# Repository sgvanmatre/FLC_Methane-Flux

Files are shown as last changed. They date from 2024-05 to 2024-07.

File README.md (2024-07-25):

# Open-source Methane Flux Instrument

Methane, a potent greenhouse gas, has significantly increased in the Earth’s atmosphere since the Industrial Revolution. A considerable portion of methane emissions stems from ground-to-atmosphere methane flux, originating from sources such as landfills, geologic seeps, and agricultural activities. These emissions exhibit spatial complexity and temporal variability, posing challenges in accurate characterization and mitigation.

Quantifying methane flux from these diverse sources is hindered by the lack of affordable measurement tools suitable for widespread deployment. There is a critical need for an instrument capable of measuring flux rates spanning 0.1 to 1000 g CH4 m-2 d-1 at landfills. The ideal instrument must operate autonomously with a remote power supply, and be compact and lightweight enough for easy transport by two individuals. It should provide flux measurements at hourly intervals and support cellular data transmission.

Through a collaborative effort between Fort Lewis College and CU Boulder's air quality laboratories, a low-cost, dynamic flux chamber was developed, calibrated, and validated for measuring methane flux within the range of 0-150 g/m²-day. Methane concentrations in the sensor chamber are monitored using four low-cost metal oxide sensors: a BME 680, along with Figaro TGS sensors (2600, 2602, and 2611).

This repository includes the PCB design and the microcontroller code for the system. 

## Table of Contents

- [Usage](#usage)
- [Contributing](#contributing)
- [Credits](#credits)
- [License](#license)
- [Updating Firmware](#updating-firmware)

## Usage

We encourage everyone to use or adapt this code for their own projects. Below are some examples and instructions to help you get started.

### Tools Used

- **Eagle PCB Software:** We used Eagle PCB software for designing and testing our printed circuit boards.
- **Arduino:** Our code is compatible with the Arduino platform and was developed using the Arduino IDE and initialized on an Arduino MKR NB 1500 board. We did have to manually update the firmware. Instruction are at the bottom of this file.

### Getting Started

1. **Clone the Repository:**
   - Clone the repository to your local machine using the following command:
     ```sh
     git clone https://github.com/your-username/your-repo-name.git
     ```

2. **Open in Eagle PCB Software:**
   - Open the Eagle PCB files from the repository in Eagle PCB software to view and modify the PCB designs.

3. **Load the Code in Arduino IDE:**
   - Open the Arduino IDE.
   - Load the Arduino code from the repository into the Arduino IDE.

4. **Upload to Your Arduino Board:**
   - Connect your Arduino board to your computer.
   - Select the correct board and port from the Arduino IDE.
   - Click the "Upload" button to upload the code to your Arduino board.

## Contributing

We welcome contributions from anyone who is interested! Whether it's fixing a bug, adding a new feature, improving documentation, or any other enhancements, your help is greatly appreciated.

### How to Contribute

1. **Fork the Repository:**
   - Click the "Fork" button at the top right of this repository page to create a copy of this repository in your GitHub account.

2. **Clone Your Fork:**
   - Clone your forked repository to your local machine using the following command:
     ```sh
     git clone https://github.com/your-username/your-repo-name.git
     ```

3. **Create a New Branch:**
   - Create a new branch to work on your changes:
     ```sh
     git checkout -b your-branch-name
     ```

4. **Make Your Changes:**
   - Implement your changes in the new branch.

5. **Commit Your Changes:**
   - Commit your changes with a clear and concise commit message:
     ```sh
     git add .
     git commit -m "Description of your changes"
     ```

6. **Push Your Changes:**
   - Push your changes to your forked repository:
     ```sh
     git push origin your-branch-name
     ```

7. **Submit a Pull Request:**
   - Go to the original repository on GitHub and click the "New Pull Request" button.
   - Select your branch from your forked repository and compare it with the base repository.
   - Submit the pull request for review.

### Guidelines

- Ensure your code follows the project's style guidelines.
- Write clear, concise commit messages.
- Update documentation as necessary.
- Test your changes thoroughly before submitting a pull request.

Thank you for your interest in contributing! Together, we can make this project even better.

## Credits

Contributors

- **Principal Contributor:** [Seth VanMatre](https://github.com/sgvanmatre)
- **Summer Contributions:** [Sonie Taylor Schermer](https://github.com/tschermer02)
- **Additional Assistance:** [Max Krauss](https://github.com/maxtkrauss)

## License

This project is licensed under the MIT License - see the LICENSE file for details.

## Firmware Update Instructions

The latest SARA-R410M-02B firmware (version -04) is now available publicly on the product page:

[Product Page - SARA-R4 Series](https://www.u-blox.com/en/product/sara-r4-series?legacy=Current#Documentation-&-resources)

A direct download to the firmware files is available here:

[Direct Download - Firmware Files](https://content.u-blox.com/sites/default/files/2023-06/SARA-R410M-02B-04-P1-L0000000512A0221-000K00.zip?_ga=2.26117621.998416448.1694721819-824184379.1689262389)

The recommended method is to update via the native USB port of the SARA-R4 module using our Windows tool "EasyFlash".

To download the correct EasyFlash tool, refer to the link in the PCN to the most up-to-date/recommended version in the section "Tools."

A link to the latest (version -04) PCN is available here:

[PCN - Version -04](https://content.u-blox.com/sites/default/files/documents/SARA-R410M-02B-04_PCN_UBX-22005059.pdf)

For updating the firmware, an application note is available here:

[Application Note - Firmware Update](https://www.u-blox.com/sites/default/files/SARA-R4-FW-Update_AppNote_UBX-17049154.pdf)

### Additional Resources for 3rd Party Boards

- **Arduino MKR NB 1500 USB test points:**
  [Forum Discussion](https://forum.arduino.cc/t/firmware-upgrade-for-ublox-sara-r410m-02b-on-the-mkr-nb-1500-2/699292)

- **Particle Boron:**
  [Community Guide](https://community.particle.io/t/how-to-load-ublox-firmware-upgrade-for-sara-r410-lte-on-the-boron/51769)

- **Sparkfun LTE M1 Shield enable USB:**
  [Hookup Guide](https://learn.sparkfun.com/tutorials/lte-cat-m1nb-iot-shield-hookup-guide?_gl=1*pm7rgo*_ga*NDUwNDc5ODYxLjE2OTMyNDMzMjk.*_ga_T369JS7J9N*MTY5NDc5ODg0My4yLjAuMTY5NDc5ODg0My42MC4wLjA.&_ga=2.145880316.975271267.1694798844-450479861.1693243329#USB-interface)

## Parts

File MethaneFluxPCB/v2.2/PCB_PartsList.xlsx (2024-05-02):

Qty | Value | Package | Parts | URL
2 | 1.0uF (https://www.digikey.com/product-detail/en/samsung-electro-mechanics/CL10A105KP8NNNC/1276-1182-1-ND/3889268) | 603 | C7, C14 | https://www.digikey.com/product-detail/en/samsung-electro-mechanics/CL10A105KP8NNNC/1276-1182-1-ND/3889268
14 | 10k (https://www.digikey.com/en/products/detail/stackpole-electronics-inc/RMCF0603JT10K0/1758104) | 603 | R14, R15, R16, R17, R20, R21, R22, R23, R24, R25, R26, R27, R28, R29 | https://www.digikey.com/en/products/detail/stackpole-electronics-inc/RMCF0603JT10K0/1758104
8 | 10uF (https://www.digikey.com/en/products/detail/samsung-electro-mechanics/CL10A106MQ8NNNC/3886777) | 603 | C5, C6, C8, C9, C20, C22, C23, C24 | https://www.digikey.com/en/products/detail/samsung-electro-mechanics/CL10A106MQ8NNNC/3886777
2 | 282836-5 (https://www.digikey.com/en/products/detail/te-connectivity-amp-connectors/282836-5/1826942) | TE_282836-5 | J1, J2 | https://www.digikey.com/en/products/detail/te-connectivity-amp-connectors/282836-5/1826942
1 | 282837-2 (https://www.digikey.com/en/products/detail/te-connectivity-amp-connectors/282836-2/1826939) | TE_282837-2 | P1 | https://www.digikey.com/en/products/detail/te-connectivity-amp-connectors/282836-2/1826939
2 | 2N7002DW (https://www.digikey.com/en/products/detail/onsemi/2N7002DW/1785764) | SOT363 | U$3, U$4 | https://www.digikey.com/en/products/detail/onsemi/2N7002DW/1785764
4 | 3.3k (https://www.digikey.com/en/products/detail/koa-speer-electronics-inc/RK73H1JRTTD3301F/12314776) | 603 | R6, R7, R8, R9 | https://www.digikey.com/en/products/detail/koa-speer-electronics-inc/RK73H1JRTTD3301F/12314776
4 | 30Ω/1.8A (https://www.digikey.com/en/products/detail/murata-electronics/BLM18EG221SN1D/1016151) | 603 | FB1, FB2, FB3, FB4 | https://www.digikey.com/en/products/detail/murata-electronics/BLM18EG221SN1D/1016151
4 | 4.7k (https://www.digikey.com/en/products/detail/yageo/RC0402JR-074K7L/726477) | 603 | R10, R11, R13, R30 | https://www.digikey.com/en/products/detail/yageo/RC0402JR-074K7L/726477
8 | 470 (https://www.digikey.com/product-detail/en/RC0603JR-07470RL/311-470GRTR-ND/726791/?itemSeq=327776216) | 603 | R1, R2, R3, R4, R5, R12, R18, R19 | https://www.digikey.com/product-detail/en/RC0603JR-07470RL/311-470GRTR-ND/726791/?itemSeq=327776216
1 | 74LVC125APW,118 (https://www.digikey.com/en/products/detail/nexperia-usa-inc/74LVC125APW-118/946678) | IC_74LVC125APW,118 | U3 | https://www.digikey.com/en/products/detail/nexperia-usa-inc/74LVC125APW-118/946678
2 | ADS1115IDGSR (https://www.digikey.com/en/products/detail/texas-instruments/ADS1115IDGSR/2231567) | SOP50P490X110-10N | U1, U5 | https://www.digikey.com/en/products/detail/texas-instruments/ADS1115IDGSR/2231567
1 | BAT-HLD-001 (https://www.digikey.com/en/products/detail/te-connectivity-linx/BAT-HLD-001/1577235) | BAT_BAT-HLD-001 | BT1 | https://www.digikey.com/en/products/detail/te-connectivity-linx/BAT-HLD-001/1577235
2 | BME680 (https://www.digikey.com/en/products/detail/bosch-sensortec/BME680/7401317) | PSON80P300X300X100-8N | U2, U4 | https://www.digikey.com/en/products/detail/bosch-sensortec/BME680/7401317
1 | DS3231/SO (https://www.digikey.com/en/products/detail/analog-devices-inc-maxim-integrated/DS3231S-T-R/1197575) | SO16W | IC1 | https://www.digikey.com/en/products/detail/analog-devices-inc-maxim-integrated/DS3231S-T-R/1197575
1 | GTFH08131YHR (https://www.digikey.com/en/products/detail/amphenol-cs-commercial-products/GTFH08131YHR/7057320) | AMPHENOL_GTFH08131YHR | J3 | https://www.digikey.com/en/products/detail/amphenol-cs-commercial-products/GTFH08131YHR/7057320
1 | IN_47UH_3.8A_SMD (https://www.digikey.com/en/products/detail/w-rth-elektronik/7447709470/1639307) | INDUCTOR_4X4MM | US1 | https://www.digikey.com/en/products/detail/w-rth-elektronik/7447709470/1639307
1 | IN_33UH_3.8A_SMD (https://www.digikey.com/en/products/detail/w-rth-elektronik/7447709470/1639307) | INDUCTOR_4X4MM | U$7 | https://www.digikey.com/en/products/detail/w%C3%BCrth-elektronik/7447709330/1638649
1 | LM2596S-5 (https://www.digikey.com/en/products/detail/texas-instruments/LM2596S-5-0-NOPB/334842) | VREG_LM2596S-5 | U6 | https://www.digikey.com/en/products/detail/texas-instruments/LM2596S-5-0-NOPB/334842
2 | LM2596S-3.3 (https://www.digikey.com/en/products/detail/texas-instruments/LM2596S-3-3/3701219) | VREG_LM2596S-3.3 | U7 | https://www.digikey.com/en/products/detail/texas-instruments/LM2596S-3-3/3701219
1 | MKRNB1500 (https://www.digikey.com/en/products/detail/arduino/ABX00019/9486709) | MRKNB1500 | U$5 | https://www.digikey.com/en/products/detail/arduino/ABX00019/9486709
1 | RB141C1100 (https://www.digikey.com/en/products/detail/e-switch/RB141C1100/3778081) | SW_RB141C1100 | S1 | https://www.digikey.com/en/products/detail/e-switch/RB141C1100/3778081
2 | Yellow (https://www.digikey.com/en/products/detail/w%C3%BCrth-elektronik/150060YS75000/4489907) | LED-0603 | D1, D3 | https://www.digikey.com/en/products/detail/w%C3%BCrth-elektronik/150060YS75000/4489907
2 | SS34_214AB (https://www.digikey.com/product-detail/en/on-semiconductor/SS34/SS34FSCT-ND/2094459) | SOD-323 | U$2, U$6 | https://www.digikey.com/product-detail/en/on-semiconductor/SS34/SS34FSCT-ND/2094459
2 | TAJC227K006RNJ (https://www.digikey.com/en/products/detail/kyocera-avx/TAJC227K006RNJ/563818) | CAPPM6032X280N | C1, C2 | https://www.digikey.com/en/products/detail/kyocera-avx/TAJC227K006RNJ/563818
2 | TAJD107K016RNJ (https://www.digikey.com/en/products/detail/kyocera-avx/TAJD107K016RNJ/563828) | CAPPM7344X310N | C3, C4 | https://www.digikey.com/en/products/detail/kyocera-avx/TAJD107K016RNJ/563828
2 | TGS2600 | TO255P920H830-4 | A1-00, A2-00
2 | TGS2602 | TGS2602 | A3-02, A4-02
2 | TGS2611 | TGS2611 | A5-11, A6-11
4 | VJ0603Y104KLXAC5G (https://www.digikey.com/en/products/detail/nextgen-components/0603B103K500SD/14632393) | CAPC1608X92N | C16, C17, C18, C19 | https://www.digikey.com/en/products/detail/nextgen-components/0603B103K500SD/14632393

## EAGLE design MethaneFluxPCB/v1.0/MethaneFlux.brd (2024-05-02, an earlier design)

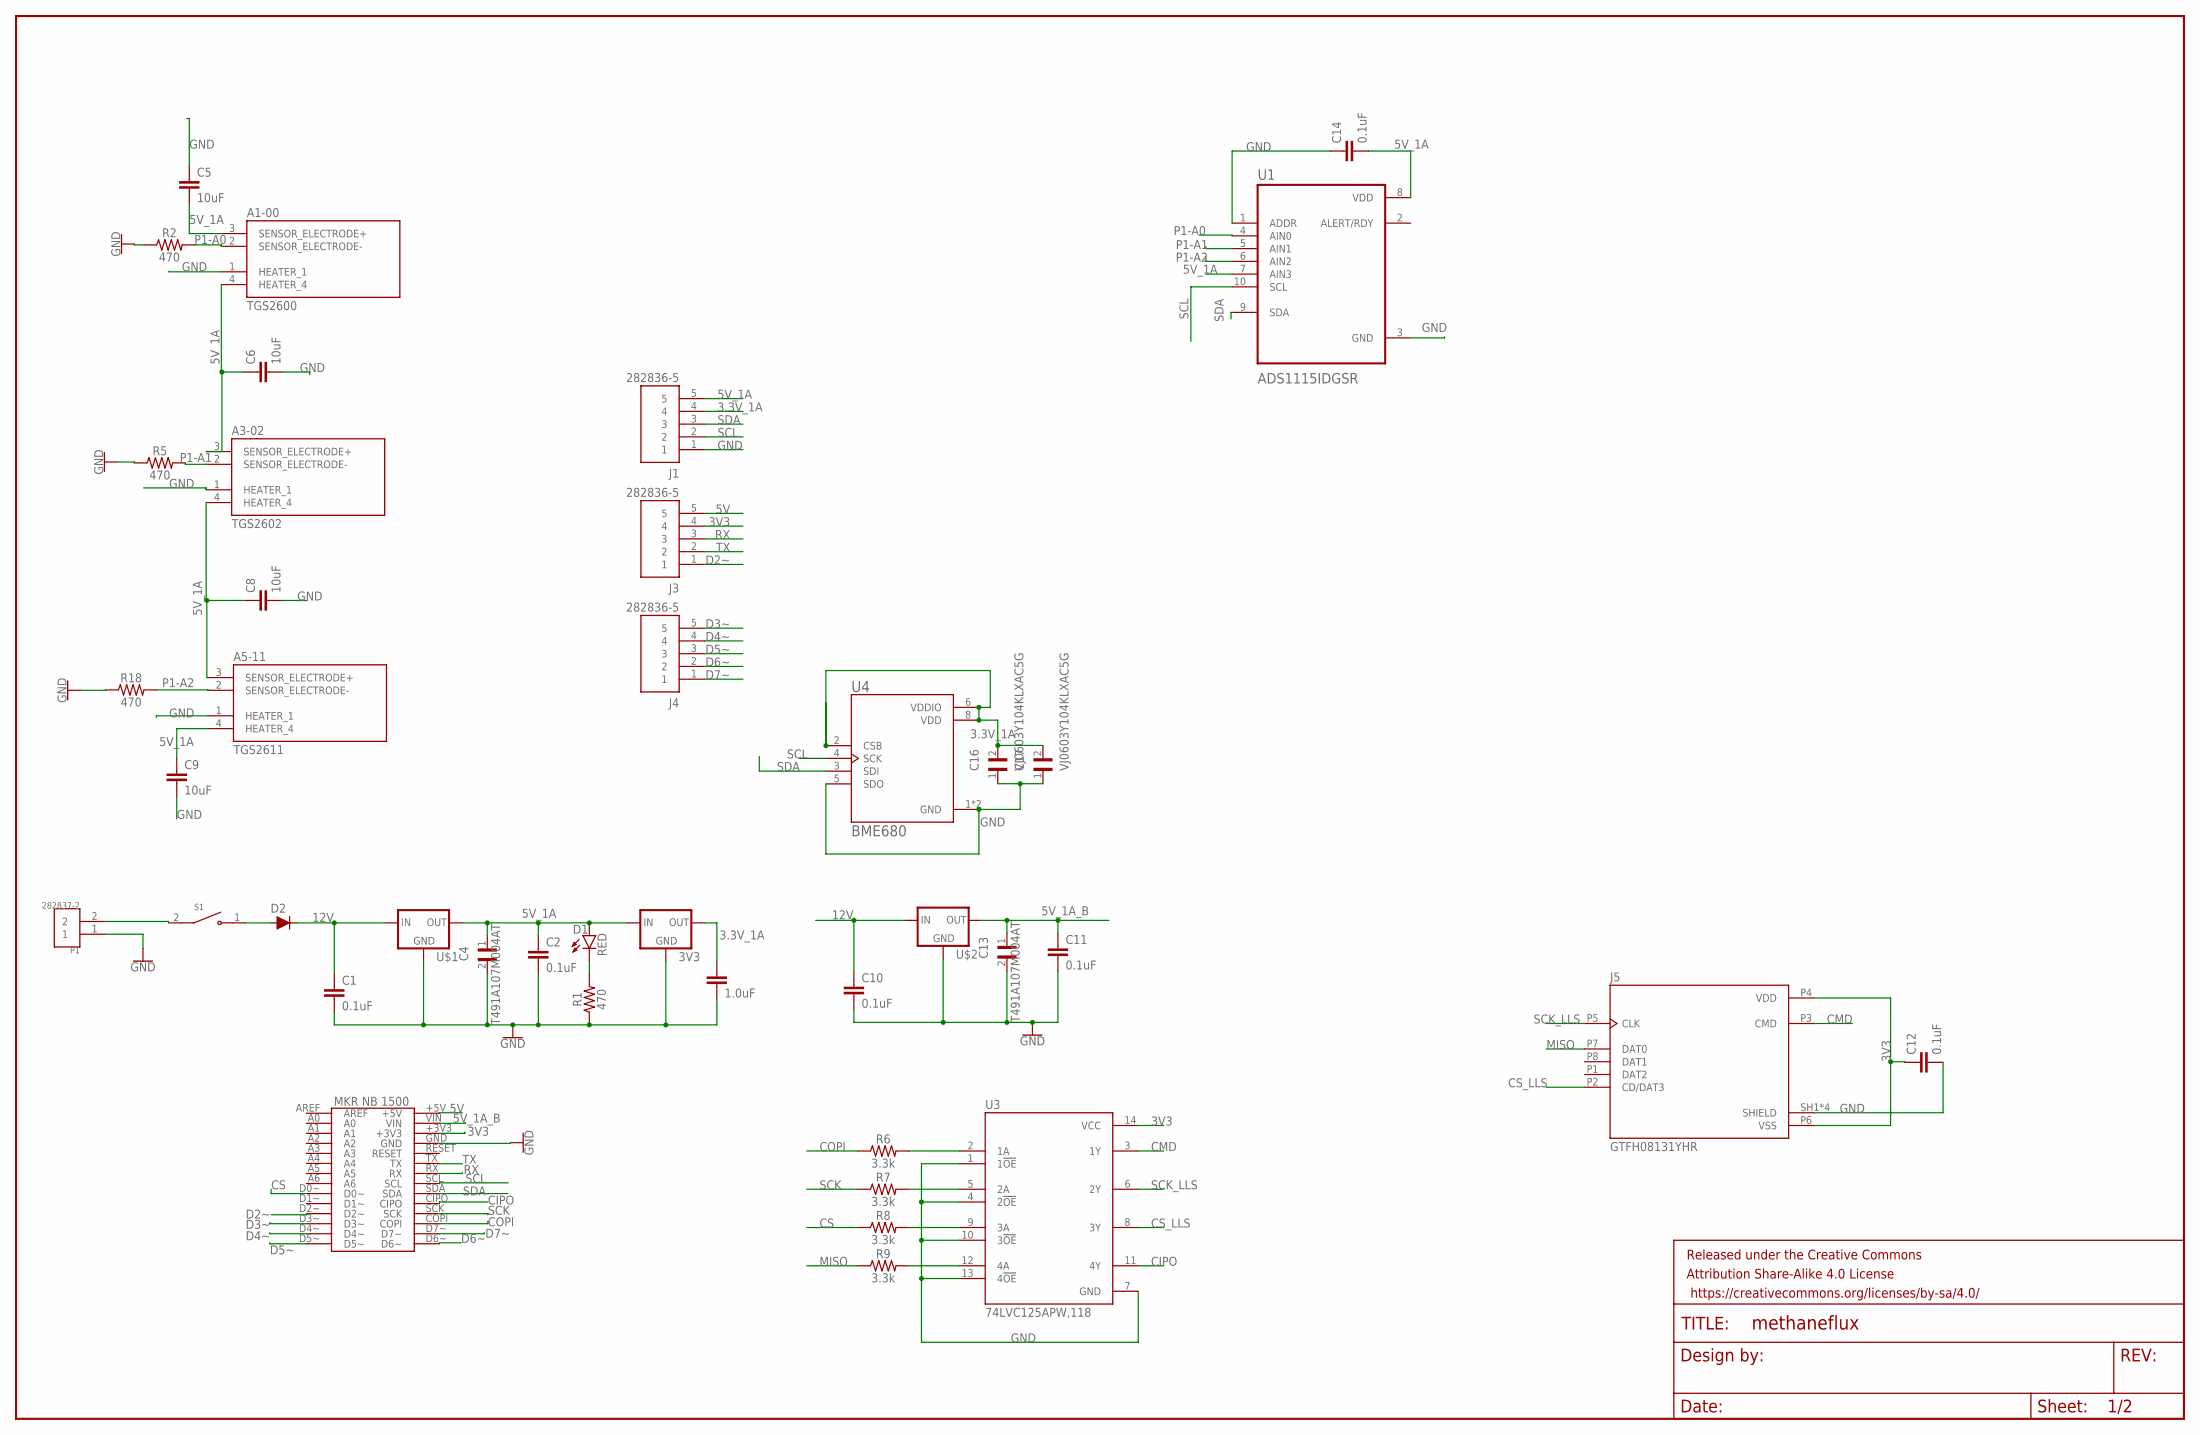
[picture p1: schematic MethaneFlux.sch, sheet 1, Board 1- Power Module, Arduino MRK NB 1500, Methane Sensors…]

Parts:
3V3: V_REG_LD1117VXXLD1117-SMD; SOT223
A1-00: TGS2600; TO255P920H830-4
A3-02: TGS2602
A5-11: TGS2611
C1, C2, C10, C11, C12, C14: 0.1uF; 0603
C3: 1.0uF; 0603
C4, C13: T491A107M004AT; CAPC3216X110N
C5, C6, C8, C9: 10uF; 0603
C16, C17: VJ0603Y104KLXAC5G; CAPC1608X92N
D1: RED; LED-0603
D2: 200mA/100V/1V; DIODE-1N4148
FRAME1: FRAME-LEDGER; CREATIVE_COMMONS
J1, J3, J4: 282836-5; TE_282836-5
J5: GTFH08131YHR; AMPHENOL_GTFH08131YHR
P1: 282837-2; TE_282837-2
R1, R2, R5, R18: 470; 0603
R6, R7, R8, R9: 3.3k; 0603
S1: RB141C1100; SW_RB141C1100
U1: ADS1115IDGSR; SOP50P490X110-10N
U3: 74LVC125APW,118; IC_74LVC125APW,118
U4: BME680; PSON80P300X300X100-8N
U$1, U$2: V_REG_LD1117VXXLD1117-SMD; SOT223
U$5: MKRNB1500; MRKNB1500

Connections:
3.3V_1A: 3V3.2 (OUT), C3.1, C16.2, C17.2, J1.4, U4.2 (CSB), U4.6 (VDDIO), U4.8 (VDD)
3V3: C12.1, J3.4, J5.P4 (VDD), J5.P6 (VSS), U3.14 (VCC), U$5.+3V3
5V: J3.5, U$5.+5V
5V_1A: 3V3.3 (IN), A1-00.3 (SENSOR_ELECTRODE+), A1-00.4 (HEATER_4), A3-02.3 (SENSOR_ELECTRODE+), A3-02.4 (HEATER_4), A5-11.3 (SENSOR_ELECTRODE+), A5-11.4 (HEATER_4), C2.1, C4.1, C5.2, C6.1, C8.1, C9.1, C14.2, D1.A, J1.5, U1.7 (AIN3), U1.8 (VDD), U$1.2 (OUT)
5V_1A_B: C11.1, C13.1, U$2.2 (OUT), U$5.VIN
12V: C1.1, C10.1, D2.C, U$1.3 (IN), U$2.3 (IN)
CIPO: U3.11 (4Y), U$5.CIPO
CMD: J5.P3 (CMD), U3.3 (1Y)
COPI: R6.1, U$5.COPI
CS: R8.1, U$5.D0~
CS_LLS: J5.P2 (CD/DAT3), U3.8 (3Y)
D2~: J3.1, U$5.D2~
D3~: J4.5, U$5.D3~
D4~: J4.4, U$5.D4~
D5~: J4.3, U$5.D5~
D6~: J4.2, U$5.D6~
D7~: J4.1, U$5.D7~
GND: 3V3.1 (GND), A1-00.1 (HEATER_1), A3-02.1 (HEATER_1), A5-11.1 (HEATER_1), C1.2, C2.2, C3.2, C4.2, C5.1, C6.2, C8.2, C9.2, C10.2, C11.2, C12.2, C13.2, C14.1, C16.1, C17.1, J1.1, J5.SH1 (SHIELD), J5.SH2 (SHIELD), J5.SH3 (SHIELD), J5.SH4 (SHIELD), P1.1, R1.1, R2.1, R5.1, R18.1, U1.1 (ADDR), U1.3 (GND), U3.1 (1!OE), U3.4 (2!OE), U3.7 (GND), U3.10 (3!OE), U3.13 (4!OE), U4.1 (GND), U4.5 (SDO), U4.7 (GND), U$1.1 (GND), U$2.1 (GND), U$5.GND
MISO: J5.P7 (DAT0), R9.1
unnamed: R6.2, U3.2 (1A)
unnamed: D1.C, R1.2
unnamed: R7.2, U3.5 (2A)
unnamed: P1.2, S1.2
unnamed: D2.A, S1.1
unnamed: R8.2, U3.9 (3A)
unnamed: R9.2, U3.12 (4A)
P1-A0: A1-00.2 (SENSOR_ELECTRODE-), R2.2, U1.4 (AIN0)
P1-A1: A3-02.2 (SENSOR_ELECTRODE-), R5.2, U1.5 (AIN1)
P1-A2: A5-11.2 (SENSOR_ELECTRODE-), R18.2, U1.6 (AIN2)
RX: J3.3, U$5.RX
SCK: R7.1, U$5.SCK
SCK_LLS: J5.P5 (CLK), U3.6 (2Y)
SCL: J1.2, U1.10 (SCL), U4.4 (SCK), U$5.SCL
SDA: J1.3, U1.9 (SDA), U4.3 (SDI), U$5.SDA
TX: J3.2, U$5.TX

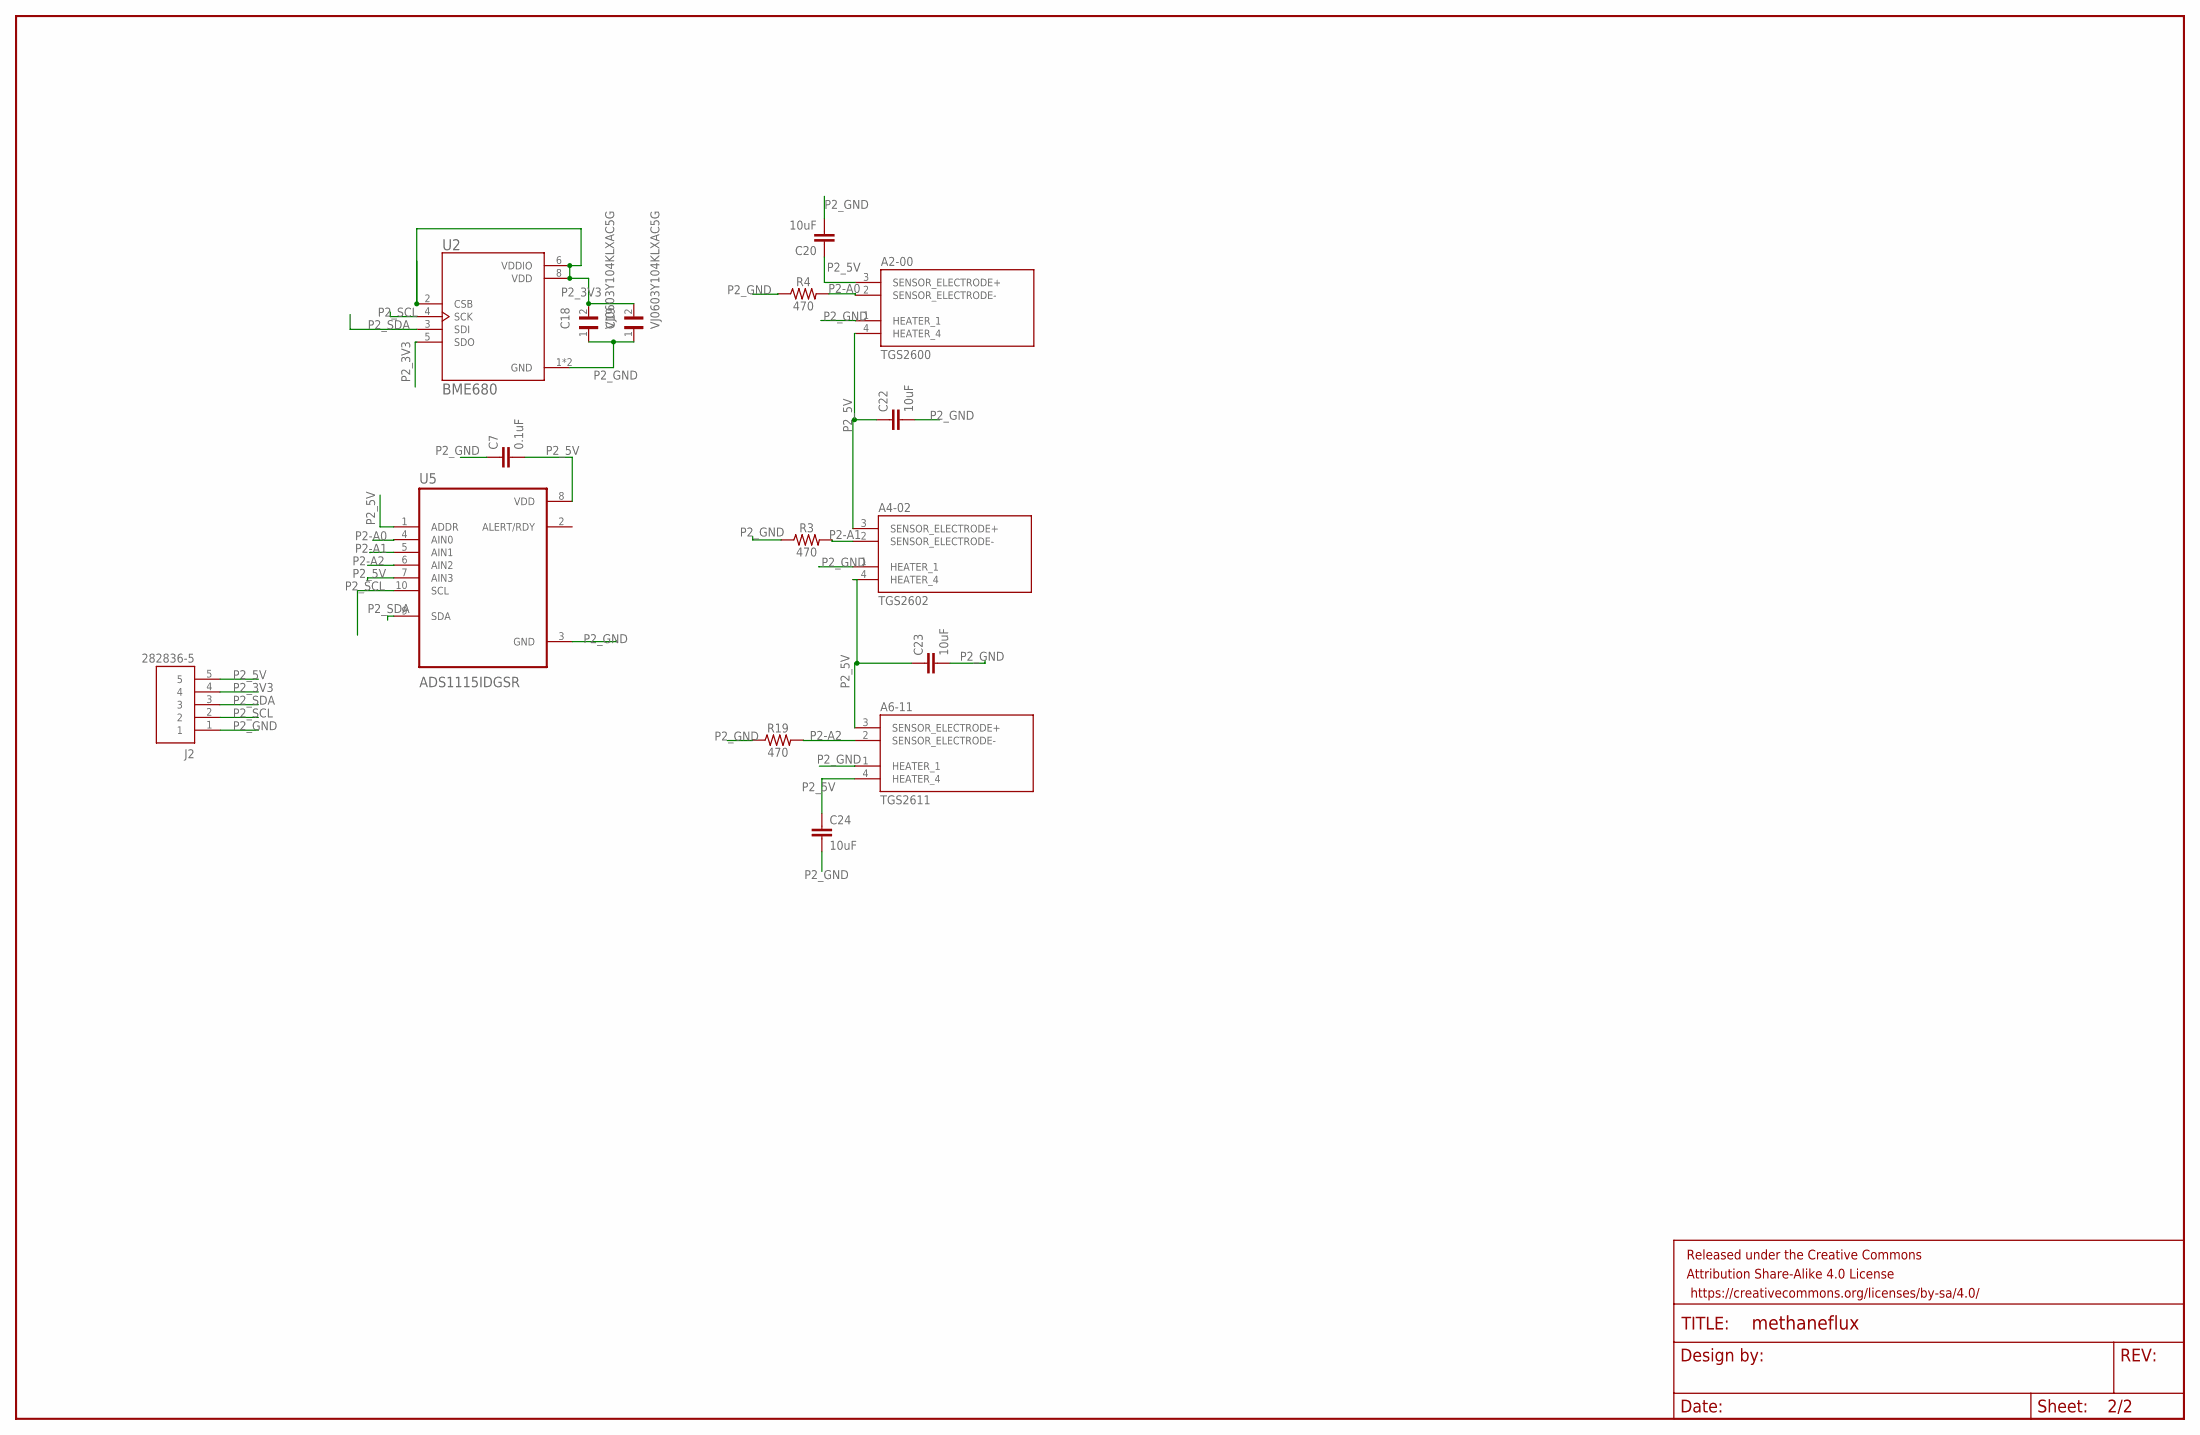
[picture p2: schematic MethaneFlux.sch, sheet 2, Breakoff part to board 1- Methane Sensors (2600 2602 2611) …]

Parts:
A2-00: TGS2600; TO255P920H830-4
A4-02: TGS2602
A6-11: TGS2611
C7: 0.1uF; 0603
C18, C19: VJ0603Y104KLXAC5G; CAPC1608X92N
C20, C22, C23, C24: 10uF; 0603
FRAME2: FRAME-LEDGER; CREATIVE_COMMONS
J2: 282836-5; TE_282836-5
R3, R4, R19: 470; 0603
U2: BME680; PSON80P300X300X100-8N
U5: ADS1115IDGSR; SOP50P490X110-10N

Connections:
P2-A0: A2-00.2 (SENSOR_ELECTRODE-), R4.2, U5.4 (AIN0)
P2-A1: A4-02.2 (SENSOR_ELECTRODE-), R3.2, U5.5 (AIN1)
P2-A2: A6-11.2 (SENSOR_ELECTRODE-), R19.2, U5.6 (AIN2)
P2_3V3: C18.2, C19.2, J2.4, U2.2 (CSB), U2.5 (SDO), U2.6 (VDDIO), U2.8 (VDD)
P2_5V: A2-00.3 (SENSOR_ELECTRODE+), A2-00.4 (HEATER_4), A4-02.3 (SENSOR_ELECTRODE+), A4-02.4 (HEATER_4), A6-11.3 (SENSOR_ELECTRODE+), A6-11.4 (HEATER_4), C7.2, C20.1, C22.1, C23.1, C24.1, J2.5, U5.1 (ADDR), U5.7 (AIN3), U5.8 (VDD)
P2_GND: A2-00.1 (HEATER_1), A4-02.1 (HEATER_1), A6-11.1 (HEATER_1), C7.1, C18.1, C19.1, C20.2, C22.2, C23.2, C24.2, J2.1, R3.1, R4.1, R19.1, U2.1 (GND), U2.7 (GND), U5.3 (GND)
P2_SCL: J2.2, U2.4 (SCK), U5.10 (SCL)
P2_SDA: J2.3, U2.3 (SDI), U5.9 (SDA)

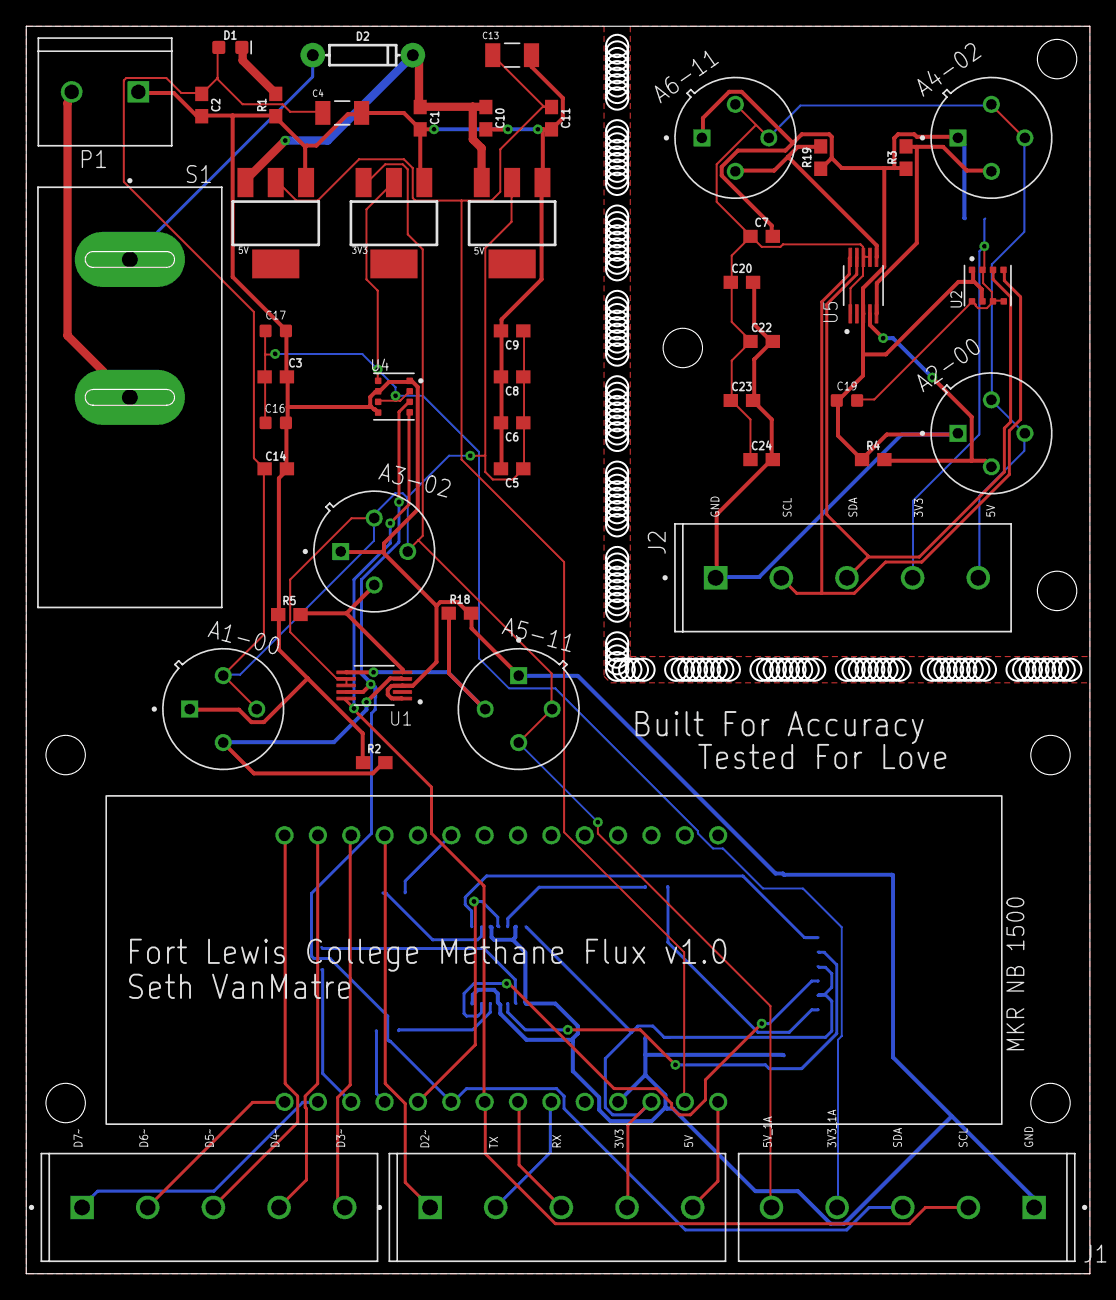
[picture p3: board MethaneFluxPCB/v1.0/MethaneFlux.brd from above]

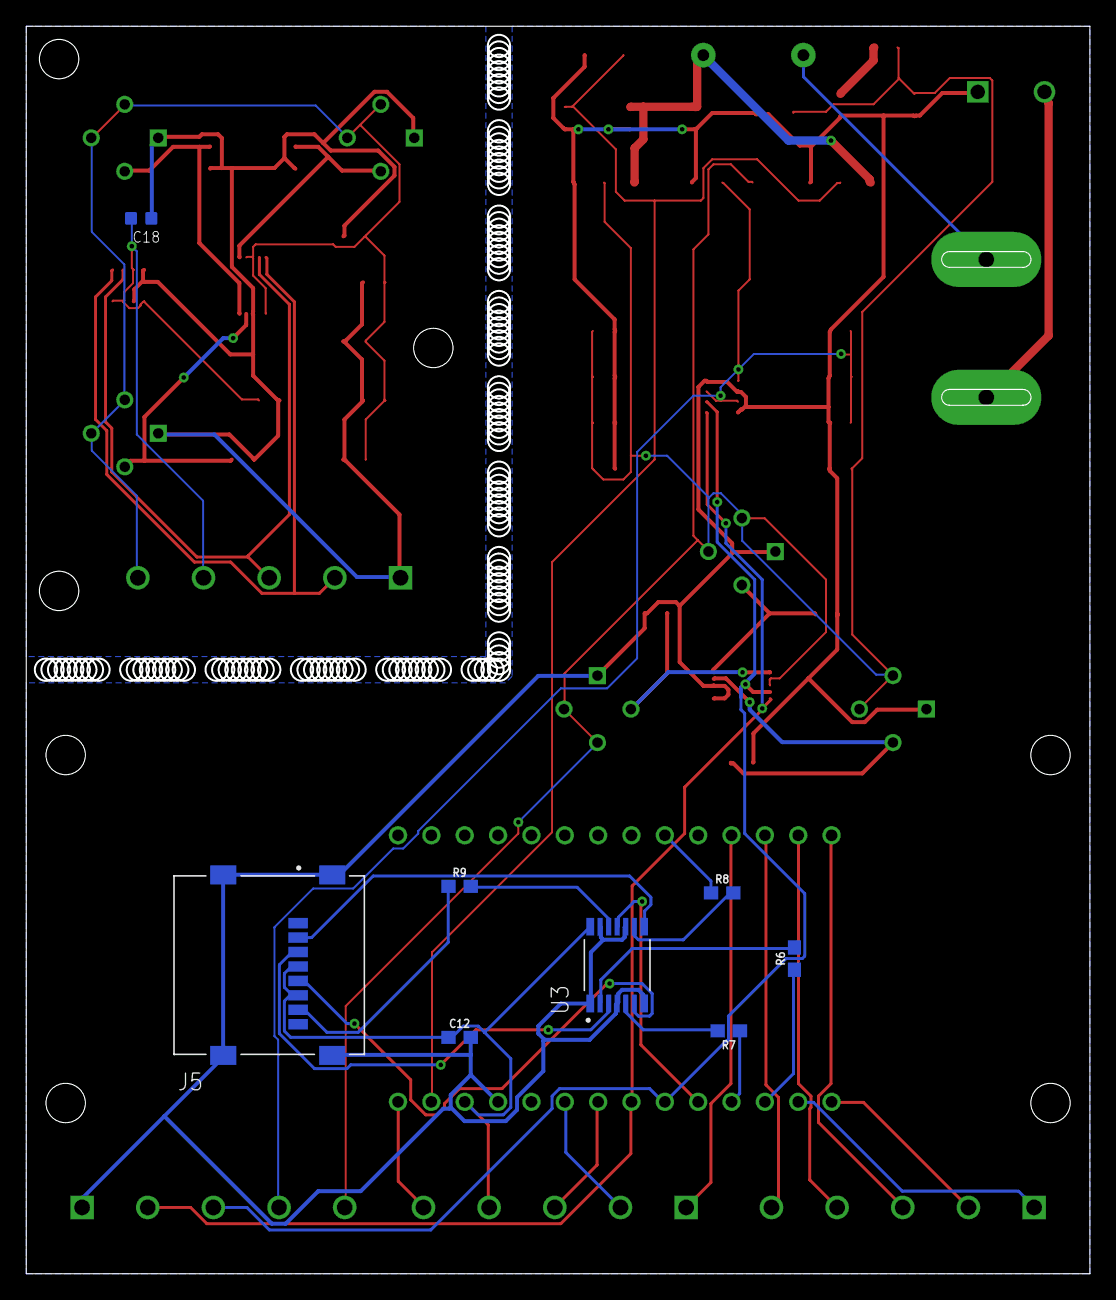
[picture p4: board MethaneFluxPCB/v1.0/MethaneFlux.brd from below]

Board: 2 copper layers, 81.0 x 95.0 mm, 59 parts (8 on the bottom side), 43 nets.

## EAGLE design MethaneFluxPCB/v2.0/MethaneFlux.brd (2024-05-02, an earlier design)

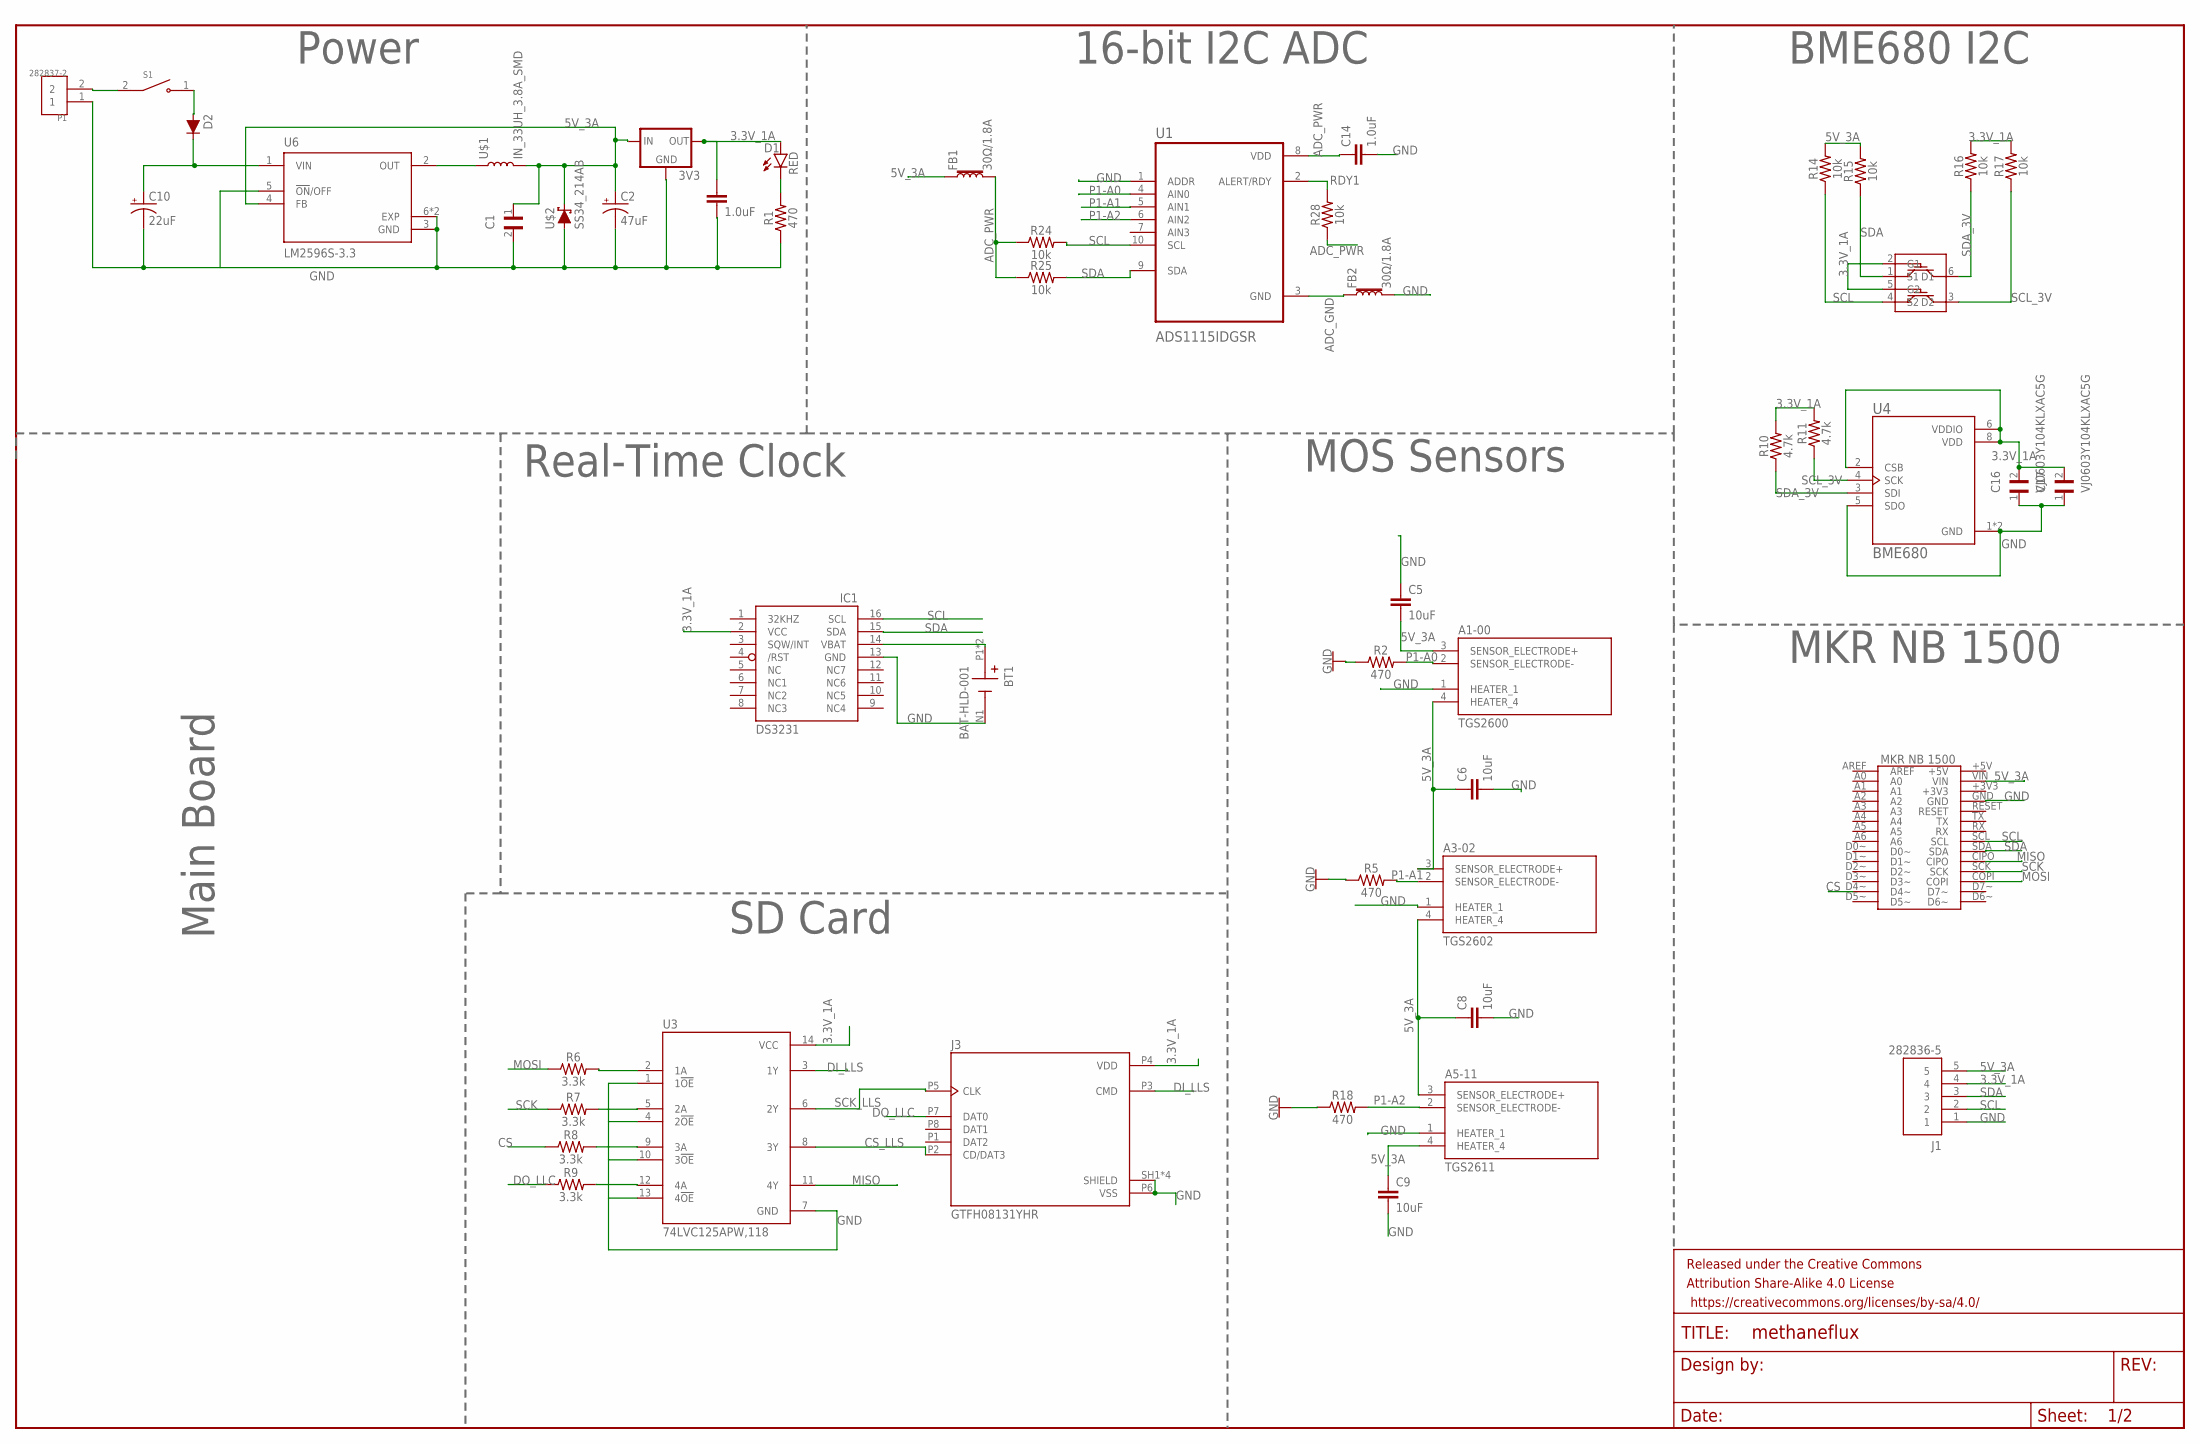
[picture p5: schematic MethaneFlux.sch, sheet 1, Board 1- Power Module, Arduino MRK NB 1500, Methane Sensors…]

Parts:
3V3: V_REG_LD1117VXXLD1117-SMD; SOT223
A1-00: TGS2600; TO255P920H830-4
A3-02: TGS2602
A5-11: TGS2611
BT1: BAT-HLD-001; BAT_BAT-HLD-001
C1: T491A107M004AT; CAPC3216X110N
C2: 47uF; PANASONIC_D
C3, C14: 1.0uF; 0603
C5, C6, C8, C9: 10uF; 0603
C10: 22uF; PANASONIC_C
C16, C17: VJ0603Y104KLXAC5G; CAPC1608X92N
D1: RED; LED-0603
D2: 200mA/100V/1V; DIODE-1N4148
FB1, FB2: 30Ω/1.8A; 0603
FRAME1: FRAME-LEDGER; CREATIVE_COMMONS
IC1: DS3231/SO; SO16W
J1: 282836-5; TE_282836-5
J3: GTFH08131YHR; AMPHENOL_GTFH08131YHR
P1: 282837-2; TE_282837-2
R1, R2, R5, R18: 470; 0603
R6, R7, R8, R9: 3.3k; 0603
R10, R11: 4.7k; 0603
R14, R15, R16, R17, R24, R25, R28: 10k; 0603
S1: RB141C1100; SW_RB141C1100
U1: ADS1115IDGSR; SOP50P490X110-10N
U3: 74LVC125APW,118; IC_74LVC125APW,118
U4: BME680; PSON80P300X300X100-8N
U6: LM2596S-3.3; VREG_LM2596S-3.3
U$1: IN_33UH_3.8A_SMD; INDUCTOR_4X4MM
U$2: SS34_214AB; SOD-323
U$3: 2N7002DW; SOT363
U$5: MKRNB1500; MRKNB1500

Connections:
3.3V_1A: 3V3.2 (OUT), C3.1, C16.2, C17.2, D1.A, IC1.2 (VCC), J1.4, J3.P4 (VDD), R10.2, R11.2, R16.2, R17.2, U3.14 (VCC), U4.2 (CSB), U4.6 (VDDIO), U4.8 (VDD), U$3.2 (G1), U$3.5 (G2)
5V_3A: 3V3.3 (IN), A1-00.3 (SENSOR_ELECTRODE+), A1-00.4 (HEATER_4), A3-02.3 (SENSOR_ELECTRODE+), A3-02.4 (HEATER_4), A5-11.3 (SENSOR_ELECTRODE+), A5-11.4 (HEATER_4), C1.1, C2.+, C5.2, C6.1, C8.1, C9.1, FB1.1, J1.5, R14.2, R15.2, U6.4 (FB), U$1.P$2 (2), U$2.C, U$5.VIN
ADC_GND: FB2.1, U1.3 (GND)
ADC_PWR: C14.1, FB1.2, R24.1, R25.1, R28.1, U1.8 (VDD)
CS: R8.1, U$5.D4~
CS_LLS: J3.P2 (CD/DAT3), U3.8 (3Y)
DI_LLS: J3.P3 (CMD), U3.3 (1Y)
DO_LLC: J3.P7 (DAT0), R9.1
GND: 3V3.1 (GND), A1-00.1 (HEATER_1), A3-02.1 (HEATER_1), A5-11.1 (HEATER_1), BT1.N1 (-), C1.2, C2.-, C3.2, C5.1, C6.2, C8.2, C9.2, C10.-, C14.2, C16.1, C17.1, FB2.2, IC1.13 (GND), J1.1, J3.P6 (VSS), J3.SH1 (SHIELD), J3.SH2 (SHIELD), J3.SH3 (SHIELD), J3.SH4 (SHIELD), P1.1, R1.1, R2.1, R5.1, R18.1, U1.1 (ADDR), U3.1 (1!OE), U3.4 (2!OE), U3.7 (GND), U3.10 (3!OE), U3.13 (4!OE), U4.1 (GND), U4.5 (SDO), U4.7 (GND), U6.3 (GND), U6.5 (!ON!/OFF), U6.6 (EXP), U6.7 (EXP), U$2.A, U$5.GND
MISO: U3.11 (4Y), U$5.CIPO
MOSI: R6.1, U$5.COPI
unnamed: R6.2, U3.2 (1A)
unnamed: P1.2, S1.2
unnamed: D2.A, S1.1
unnamed: R7.2, U3.5 (2A)
unnamed: R8.2, U3.9 (3A)
unnamed: R9.2, U3.12 (4A)
unnamed: U6.2 (OUT), U$1.P$1 (1)
unnamed: BT1.P1 (+), BT1.P2 (+), IC1.14 (VBAT)
unnamed: C10.+, D2.C, U6.1 (VIN)
unnamed: D1.C, R1.2
P1-A0: A1-00.2 (SENSOR_ELECTRODE-), R2.2, U1.4 (AIN0)
P1-A1: A3-02.2 (SENSOR_ELECTRODE-), R5.2, U1.5 (AIN1)
P1-A2: A5-11.2 (SENSOR_ELECTRODE-), R18.2, U1.6 (AIN2)
RDY1: R28.2, U1.2 (ALERT/RDY)
SCK: R7.1, U$5.SCK
SCK_LLS: J3.P5 (CLK), U3.6 (2Y)
SCL: IC1.16 (SCL), J1.2, R14.1, R24.2, U1.10 (SCL), U$3.4 (S2), U$5.SCL
SCL_3V: R11.1, R17.1, U4.4 (SCK), U$3.3 (D2)
SDA: IC1.15 (SDA), J1.3, R15.1, R25.2, U1.9 (SDA), U$3.1 (S1), U$5.SDA
SDA_3V: R10.1, R16.1, U4.3 (SDI), U$3.6 (D1)

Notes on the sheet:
MKR NB 1500
MOS Sensors
BME680 I2C
16-bit I2C ADC
Power
Real-Time Clock
SD Card
Main Board

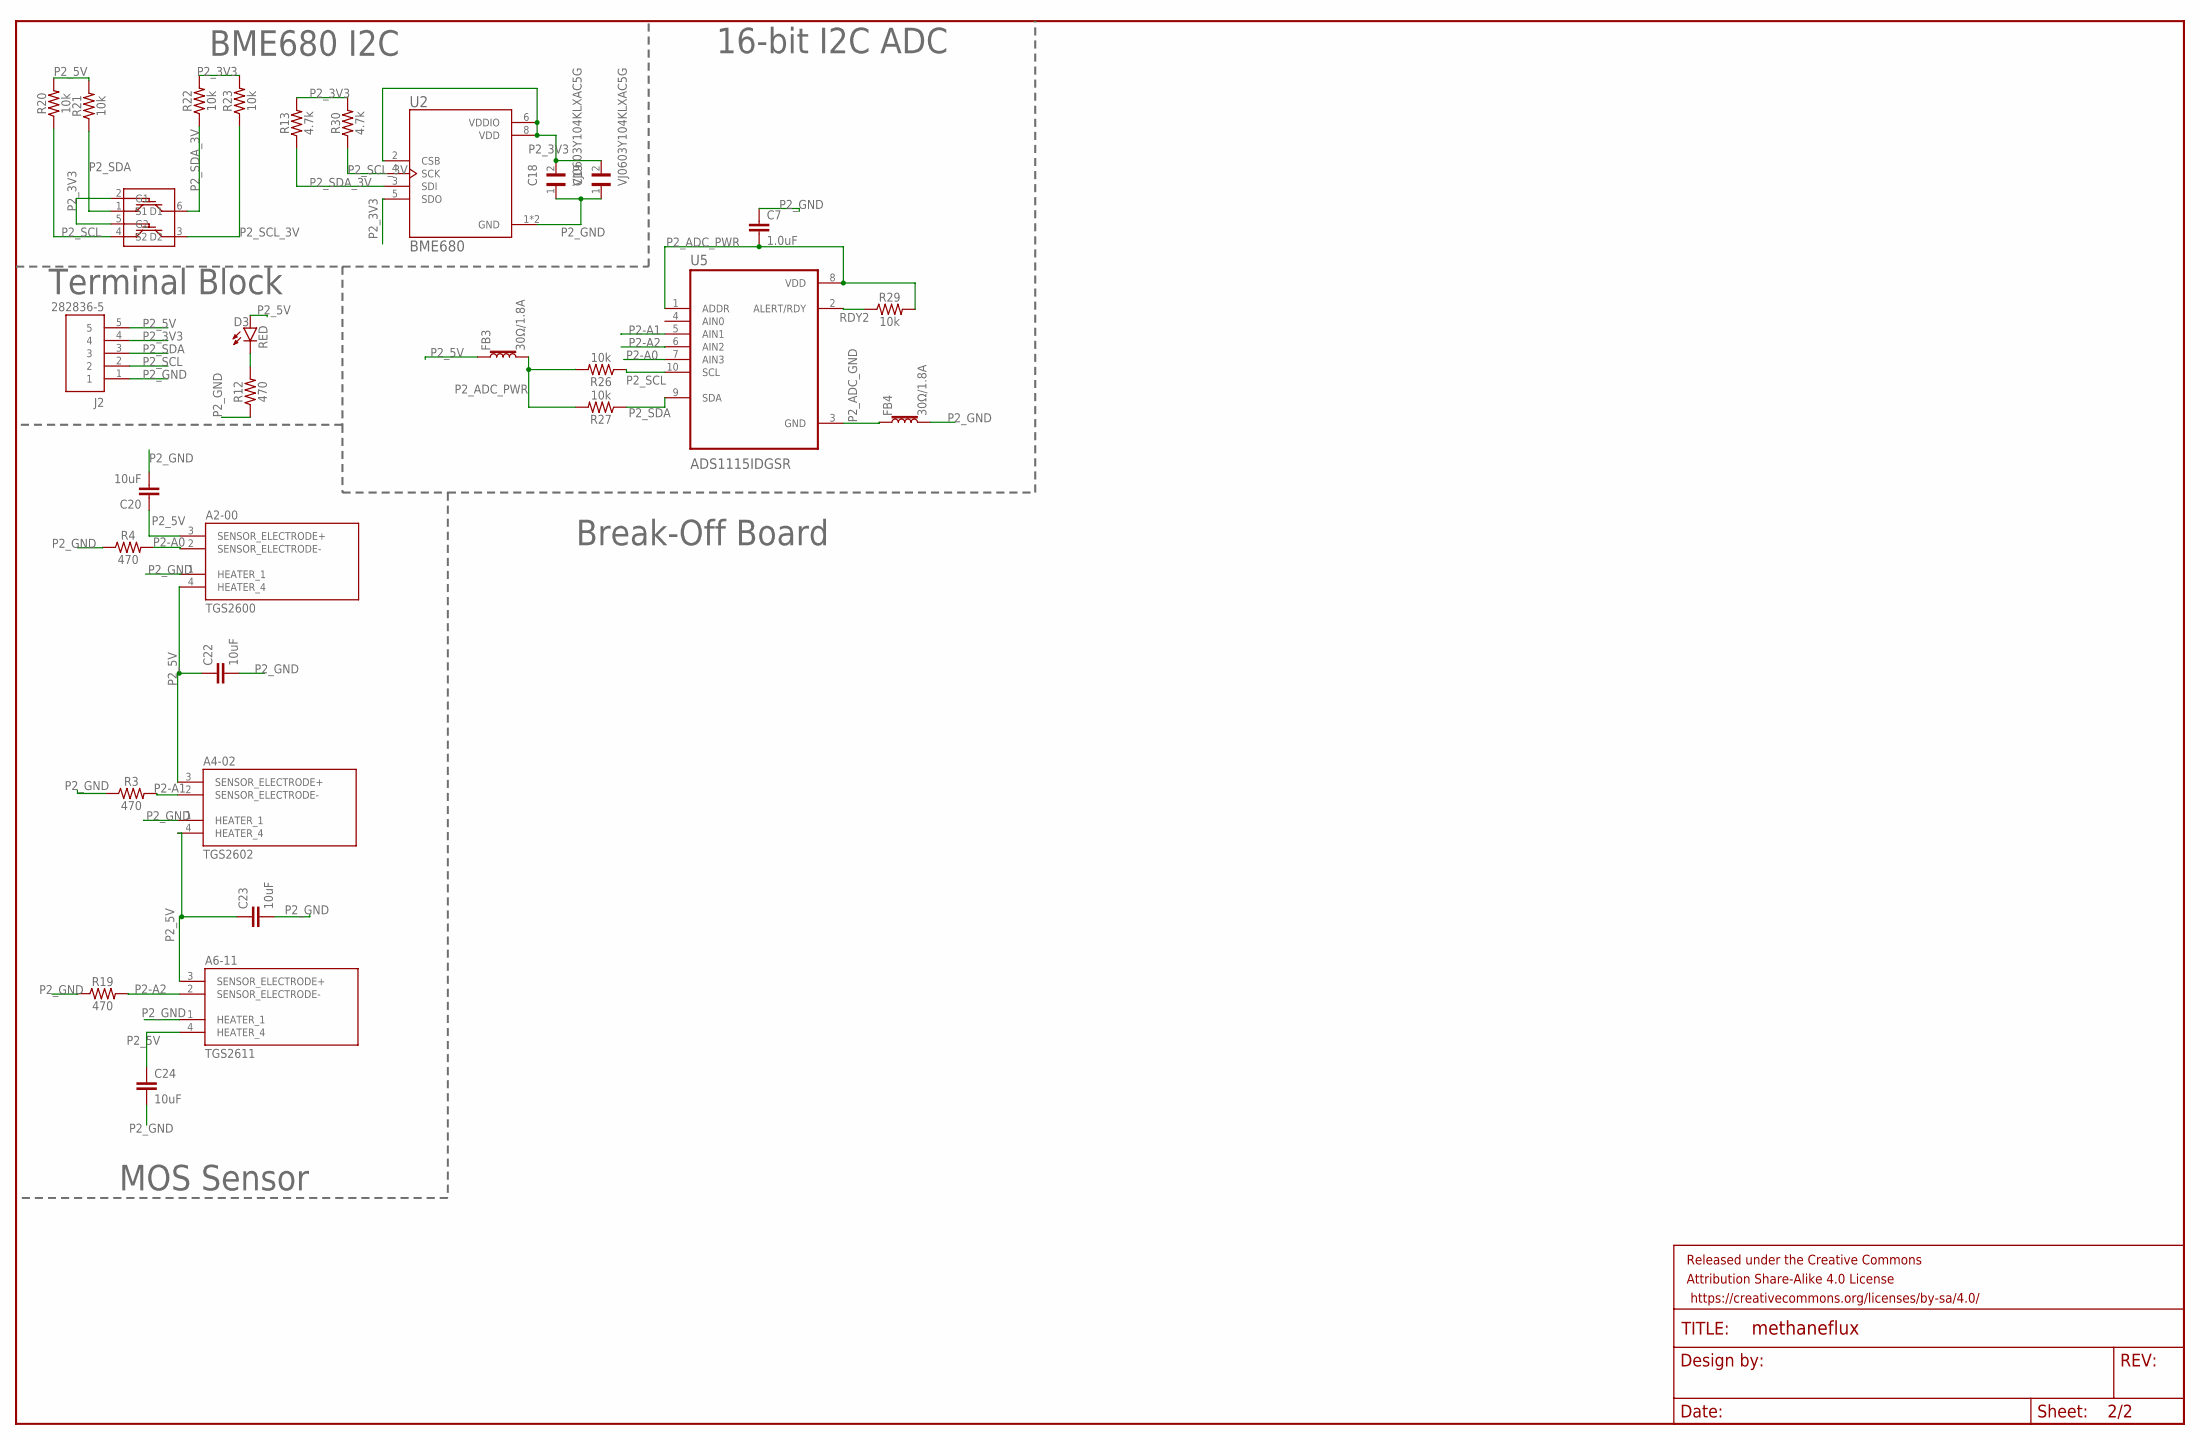
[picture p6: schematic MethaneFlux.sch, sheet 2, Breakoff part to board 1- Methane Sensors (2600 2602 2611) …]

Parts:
A2-00: TGS2600; TO255P920H830-4
A4-02: TGS2602
A6-11: TGS2611
C7: 1.0uF; 0603
C18, C19: VJ0603Y104KLXAC5G; CAPC1608X92N
C20, C22, C23, C24: 10uF; 0603
D3: RED; LED-0603
FB3, FB4: 30Ω/1.8A; 0603
FRAME2: FRAME-LEDGER; CREATIVE_COMMONS
J2: 282836-5; TE_282836-5
R3, R4, R12, R19: 470; 0603
R13, R30: 4.7k; 0603
R20, R21, R22, R23, R26, R27, R29: 10k; 0603
U2: BME680; PSON80P300X300X100-8N
U5: ADS1115IDGSR; SOP50P490X110-10N
U$4: 2N7002DW; SOT363

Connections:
unnamed: D3.C, R12.2
P2-A0: A2-00.2 (SENSOR_ELECTRODE-), R4.2, U5.7 (AIN3)
P2-A1: A4-02.2 (SENSOR_ELECTRODE-), R3.2, U5.5 (AIN1)
P2-A2: A6-11.2 (SENSOR_ELECTRODE-), R19.2, U5.6 (AIN2)
P2_3V3: C18.2, C19.2, J2.4, R13.2, R22.2, R23.2, R30.2, U2.2 (CSB), U2.5 (SDO), U2.6 (VDDIO), U2.8 (VDD), U$4.2 (G1), U$4.5 (G2)
P2_5V: A2-00.3 (SENSOR_ELECTRODE+), A2-00.4 (HEATER_4), A4-02.3 (SENSOR_ELECTRODE+), A4-02.4 (HEATER_4), A6-11.3 (SENSOR_ELECTRODE+), A6-11.4 (HEATER_4), C20.1, C22.1, C23.1, C24.1, D3.A, FB3.1, J2.5, R20.2, R21.2
P2_ADC_GND: FB4.1, U5.3 (GND)
P2_ADC_PWR: C7.2, FB3.2, R26.2, R27.2, R29.2, U5.1 (ADDR), U5.8 (VDD)
P2_GND: A2-00.1 (HEATER_1), A4-02.1 (HEATER_1), A6-11.1 (HEATER_1), C7.1, C18.1, C19.1, C20.2, C22.2, C23.2, C24.2, FB4.2, J2.1, R3.1, R4.1, R12.1, R19.1, U2.1 (GND), U2.7 (GND)
P2_SCL: J2.2, R20.1, R26.1, U5.10 (SCL), U$4.4 (S2)
P2_SCL_3V: R23.1, R30.1, U2.4 (SCK), U$4.3 (D2)
P2_SDA: J2.3, R21.1, R27.1, U5.9 (SDA), U$4.1 (S1)
P2_SDA_3V: R13.1, R22.1, U2.3 (SDI), U$4.6 (D1)
RDY2: R29.1, U5.2 (ALERT/RDY)

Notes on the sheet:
MOS Sensor
Terminal Block
BME680 I2C
16-bit I2C ADC
Break-Off Board

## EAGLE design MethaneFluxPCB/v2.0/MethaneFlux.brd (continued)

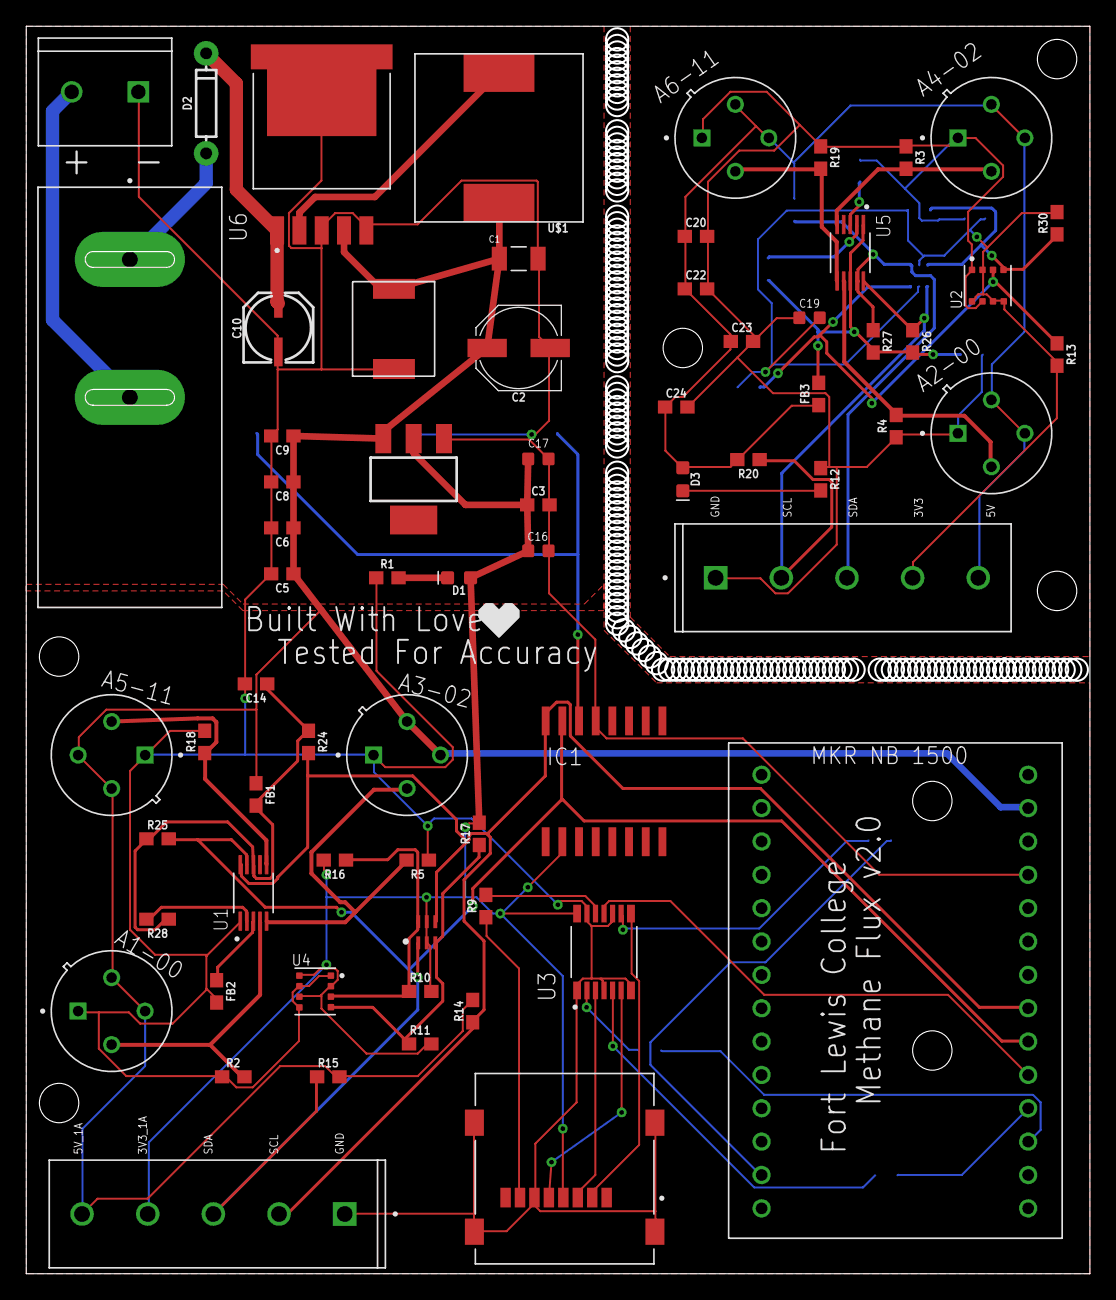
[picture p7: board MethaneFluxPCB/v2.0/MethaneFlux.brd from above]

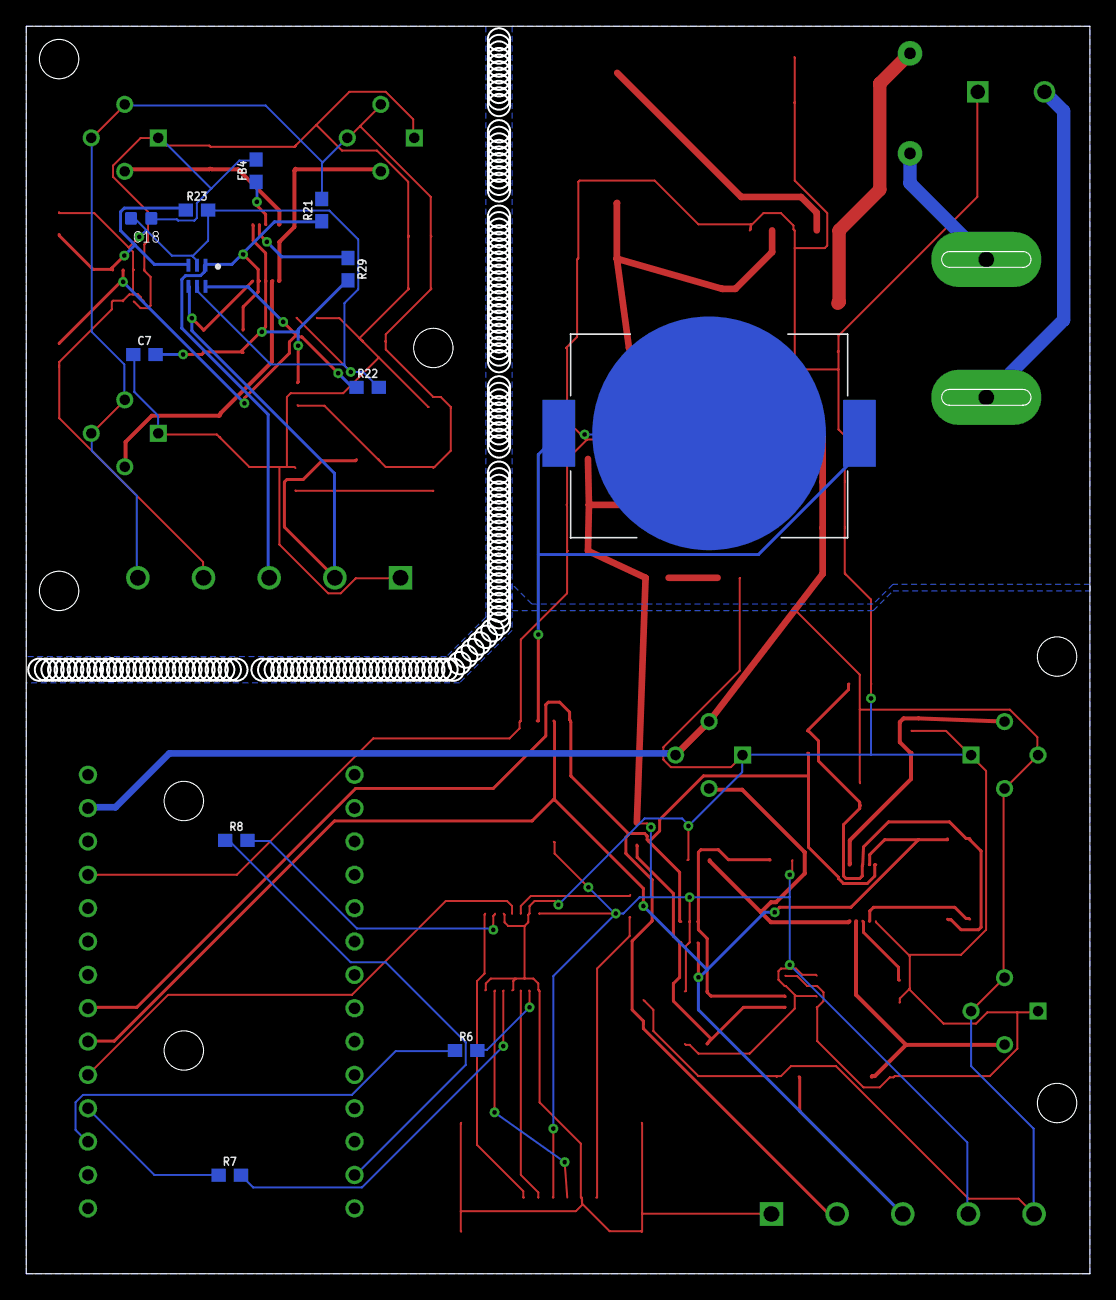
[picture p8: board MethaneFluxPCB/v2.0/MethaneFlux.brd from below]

Board: 2 copper layers, 81.0 x 95.0 mm, 82 parts (12 on the bottom side), 45 nets.

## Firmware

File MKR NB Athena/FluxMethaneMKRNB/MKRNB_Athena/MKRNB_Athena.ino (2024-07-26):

#include <ArduinoHttpClient.h>
#include <ArduinoJson.h>
#include <MKRNB.h>
#include <Wire.h>
#include <Adafruit_Sensor.h>
#include "Adafruit_BME680.h"
#include "ADS1X15.h"
#include <SensirionI2cSfmSf06.h>
#include <SPI.h>
#include <SD.h>
#include <RTCZero.h>

// macro definitions -------------------------------------
// make sure that we use the proper definition of NO_ERROR
#ifdef NO_ERROR
#undef NO_ERROR
#endif
#define NO_ERROR 0

static char errorMessage[64];
static int16_t error;

SensirionI2cSfmSf06 sensor;

// -----------------------BME DEF-----------------------------
#define SEALEVELPRESSURE_HPA (1013.25)
#define BME_A_ADDRESS 0x76
#define BME_B_ADDRESS 0x77
Adafruit_BME680 A_bme; 
Adafruit_BME680 B_bme;

// -----------------------ADC DEF-----------------------------
ADS1115 A_ADS(0x48);
ADS1115 B_ADS(0x49);

// ----------------------- SD Card ---------------------------
const int chipSelect = 4;  // SD card CS pin

// Debug options
#define PRINT_AT        true   // Show or hide AT command output from the modem

// PIN Number
const char PINNUMBER[]     = "";
char apn[] = "soracom.io";
char user[] = "sora";
char pass[] = "sora";

// Server details
const char server[] = "unified.soracom.io";
const int  port = 80; 


NBClient client;
GPRS gprs;
NB nbAccess(PRINT_AT);
HttpClient http(client, server, port);

// Init on-board RTC
RTCZero rtc;

// connection state
bool connected = false;

// Publish interval
long previousMillis = 0; 
long interval = 20000; // milliseconds

void setup() {
    //Initialize serial
  Serial.begin(115200);
  delay(5000);

  // ------------ SD Card -----------------
  Serial.println("Initializing SD card...");

  // See if the card is present and can be initialized:
  if (!SD.begin(chipSelect)) {
    Serial.println("SD Card initialization failed, or not present");
    delay(500);
    Serial.println("Data will not be written to SD Card");
  }
  else{
    Serial.println("SD Card initialized.");
  }

  
  // ----------------------- BME -----------------------------
  if(!A_bme.begin(BME_A_ADDRESS)){
    Serial.println("Could not find valid BME Ambiant Sensor..."); 
    }
  if(!B_bme.begin(BME_B_ADDRESS)){
    Serial.println("Could not find valid BME Main Sensor...");
    }
   Serial.println("BME Started");
    
  // Set up oversampling and filter initialization ^bme1 and bme2^ 
  A_bme.setTemperatureOversampling(BME680_OS_8X);
  A_bme.setHumidityOversampling(BME680_OS_8X);
  A_bme.setPressureOversampling(BME680_OS_NONE);
  A_bme.setIIRFilterSize(BME680_FILTER_SIZE_3);
  A_bme.setGasHeater(320, 150); // 320*C for 150 ms

  B_bme.setTemperatureOversampling(BME680_OS_8X);
  B_bme.setHumidityOversampling(BME680_OS_8X);
  B_bme.setPressureOversampling(BME680_OS_NONE);
  B_bme.setIIRFilterSize(BME680_FILTER_SIZE_3);
  B_bme.setGasHeater(320, 150); // 320*C for 150 ms

  // ----------------------- ADC -----------------------------
  A_ADS.begin();
  A_ADS.setGain(0);
  
  B_ADS.begin();
  B_ADS.setGain(0);

// ----------------------- GMS Setup -----------------------------
  pinMode(SARA_RESETN, OUTPUT);
  digitalWrite(SARA_RESETN, LOW);
  pinMode(SARA_PWR_ON, OUTPUT);
  
  // Wait for port to open
  start_and_connect_modem();

  //    ----------------------- FML -----------------------------
    sensor.begin(Wire, SFM4300_I2C_ADDR_2A);
    Serial.println("Connection to Flow");

    sensor.stopContinuousMeasurement();
    delay(100);
    uint32_t productIdentifier = 0;
    uint8_t serialNumber[8] = {0};
    error = sensor.readProductIdentifier(productIdentifier, serialNumber, 8);
    Serial.println(error);
    if (error != NO_ERROR) {
        Serial.print("Error trying to execute readProductIdentifier(): ");
        errorToString(error, errorMessage, sizeof errorMessage);
        Serial.println(errorMessage);
        return;
    }
    Serial.print("productIdentifier: ");
    Serial.print(productIdentifier);
    Serial.print("\t");
    Serial.print("serialNumber: ");
    print_byte_array(serialNumber, 8);
    Serial.println();
    error = sensor.startO2ContinuousMeasurement();
    if (error != NO_ERROR) {
        Serial.print(
            "Error trying to execute startO2ContinuousMeasurement(): ");
        errorToString(error, errorMessage, sizeof errorMessage);
        Serial.println(errorMessage);
        return;
    }

    Serial.println("Flow Started");

  Serial.println("End of startup"); 
  
}

void loop() {
  unsigned long currentMillis = millis(); 

    //----------------------- BME READING -----------------------------
  A_bme.performReading();
  delay(10);
  B_bme.performReading();
  delay(10);
  
  // ----------------------- ADC READING -----------------------------
  int16_t A_TGS00 = A_ADS.readADC(0);
  delay(10);
  int16_t A_TGS02 = A_ADS.readADC(1);
  delay(10);
  int16_t A_TGS11 = A_ADS.readADC(2);
  delay(10);

  int16_t B_TGS00 = B_ADS.readADC(3);
  delay(10);
  int16_t B_TGS02 = B_ADS.readADC(1);
  delay(10);
  int16_t B_TGS11 = B_ADS.readADC(2);
  delay(10);

  // -------------------- Flow Meter READING --------------------------
    float aFlow = 0.0;
    float aTemperature = 0.0;
    uint16_t aStatusWord = 0u;
    delay(100);
    error = sensor.readMeasurementData(aFlow, aTemperature, aStatusWord);
    if (error != NO_ERROR) {
        Serial.print("Error trying to execute readMeasurementData(): ");
        errorToString(error, errorMessage, sizeof errorMessage);
        Serial.println(errorMessage);
        return;
    }
  
  // ----------------------- Send Data to SD card -----------------
  delay(100);
  logDataToSD(currentMillis, aFlow, aTemperature, A_bme.temperature, A_bme.humidity, A_bme.pressure, A_bme.gas_resistance / 1000.0, A_TGS00, A_TGS02, A_TGS11, B_bme.temperature, B_bme.humidity, B_bme.pressure, B_bme.gas_resistance / 1000.0, B_TGS00, B_TGS02, B_TGS11);
  delay(100);

  // ----------------------- Send data to SoraCOM ------------------
  // Make sure the device is still connected to CatM network
  if (nbAccess.isAccessAlive()) {
    Serial.println("Sending..."); 
      // Construct the JSON data to send
      StaticJsonDocument<200> doc;
      doc["aFlow"] = aFlow;
      doc["aTemp"] = aTemperature;
      doc["A_TEMP"] = A_bme.temperature;
      doc["A_Humidity"] = A_bme.humidity;
      doc["A_Pressure"] = A_bme.pressure;
      doc["A_Gas"] = A_bme.gas_resistance / 1000.0;
      doc["A_TGS00"] = A_TGS00;
      doc["A_TGS02"] = A_TGS02;
      doc["A_TGS11"] = A_TGS11;
      doc["B_TEMP"] = B_bme.temperature;
      doc["B_Humidity"] = B_bme.humidity;
      doc["B_Pressure"] = B_bme.pressure;
      doc["B_Gas"] = B_bme.gas_resistance / 1000.0;
      doc["B_TGS00"] = B_TGS00;
      doc["B_TGS02"] = B_TGS02;
      doc["B_TGS11"] = B_TGS11;
      char jsonBuffer[512];
      serializeJson(doc, jsonBuffer); // print to client
      post_data(jsonBuffer); 

  } else {
    Serial.println("Modem disconnected, reconnecting");
    connected = false;
    //connect_modem();
  }

  delay(5000); 
}

// ------------------------ SD Card Writing ----------------------------
void logDataToSD(unsigned long currentMillis, float aFlow, float aTemperature, float A_TEMP, float A_Humidity, float A_Pressure, float A_Gas, int16_t A_TGS00, int16_t A_TGS02, int16_t A_TGS11, float B_TEMP, float B_Humidity, float B_Pressure, float B_Gas, int16_t B_TGS00, int16_t B_TGS02, int16_t B_TGS11) {
  // boolean for writing column headers
  bool fileExists = SD.exists("datalog.csv");
  // Open the file for appending
  File dataFile = SD.open("datalog.csv", FILE_WRITE);
  // if file does not exist yet (fileExists == FALSE), write preset column headers
  if (!fileExists) {
    dataFile.println("Year-Month-Day Hour/Min/Sec,Flux Chamber,aFlow,aTemperature,A_Temperature,A_Humidity,A_Pressure,A_Gas,A_TGS00,A_TGS02,A_TGS11,B_Temperature,B_Humidity,B_Pressure,B_Gas,B_TGS00,B_TGS02,B_TGS11");
    Serial.println("Header written to SD card");
  } 

  // If the file is open, write to it
  if (dataFile) {
    // Read current time from RTC
    int currentSeconds = rtc.getSeconds();
    int currentMinutes = rtc.getMinutes();
    int currentHours = rtc.getHours();
    int currentDay = rtc.getDay();
    int currentMonth = rtc.getMonth();
    int currentYear = rtc.getYear();
    // Write the data
    dataFile.print(String(currentYear) + "-" + String(currentMonth) + "-" + String(currentDay) + " " + String(currentHours) + ":" +
                     String(currentMinutes) + ":" + String(currentSeconds));
    dataFile.print(",");
    dataFile.print("1"); // Need to change to whichever flux chamber you are running
    dataFile.print(",");
    dataFile.print(aFlow);
    dataFile.print(",");
    dataFile.print(aTemperature);
    dataFile.print(",");
    dataFile.print(A_TEMP);
    dataFile.print(",");
    dataFile.print(A_Humidity);
    dataFile.print(",");
    dataFile.print(A_Pressure);
    dataFile.print(",");
    dataFile.print(A_Gas);
    dataFile.print(",");
    dataFile.print(A_TGS00);
    dataFile.print(",");
    dataFile.print(A_TGS02);
    dataFile.print(",");
    dataFile.print(A_TGS11);
    dataFile.print(",");
    dataFile.print(B_TEMP);
    dataFile.print(",");
    dataFile.print(B_Humidity);
    dataFile.print(",");
    dataFile.print(B_Pressure);
    dataFile.print(",");
    dataFile.print(B_Gas);
    dataFile.print(",");
    dataFile.print(B_TGS00);
    dataFile.print(",");
    dataFile.print(B_TGS02);
    dataFile.print(",");
    dataFile.print(B_TGS11);
    dataFile.println();
    dataFile.close();
    Serial.println("Data written to SD card");
  } else {
    Serial.println("Error opening datalog.csv");
  }
}

// --------------------------- Cellular ---------------------------
void post_data(String postData) {
  Serial.println("making POST request");
  String contentType = "application/json";

  http.post("/", contentType, postData);

  // read the status code and body of the response
  int statusCode = http.responseStatusCode();
  String response = http.responseBody();

  Serial.print("Status code: ");
  Serial.println(statusCode);
  Serial.print("Response: ");
  Serial.println(response);
}

void start_and_connect_modem(){
  // Send Poweron pulse
  digitalWrite(SARA_PWR_ON, HIGH);
  delay(300);
  digitalWrite(SARA_PWR_ON, LOW);
  delay(1000);
  // Turn on the modem
  if (Serial) Serial.print(">>> Turning on modem...");
  if (MODEM.begin()) {
    if (Serial) Serial.println(" done!");
  } else {
    if (Serial) Serial.println(" error, could not turn on modem! Try power-cycling.");
    return;
  }

  while (!MODEM.noop());
  MODEM.sendf("ATI9");
  MODEM.waitForResponse(2000);
  
  // Run AT commands to reset the modem to global default settings
  Serial.print(">>> Resetting modem to default settings...");
  MODEM.sendf("AT+CFUN=0");
  MODEM.waitForResponse(6000);
  MODEM.sendf("AT+UMNOPROF=2");
  MODEM.waitForResponse(6000);
  MODEM.sendf("AT+CFUN=15");
  MODEM.waitForResponse(6000);
  MODEM.sendf("AT+CFUN=0");
  MODEM.waitForResponse(6000);
  MODEM.sendf("AT+UMNOPROF=0");
  MODEM.waitForResponse(6000);
  MODEM.sendf("AT+CFUN=15");
  MODEM.waitForResponse(6000);
  MODEM.sendf("AT+URAT=7");
  MODEM.waitForResponse(6000);
  MODEM.sendf("AT+UBANDMASK?");
  MODEM.waitForResponse(6000);
  Serial.println(" done!");
  
  delay(2000);
  // attempt to connect to GSM and GPRS:
  Serial.print("Attempting to connect to GSM and GPRS");
   
  connect_modem();
  
}

void connect_modem(){
  // After starting the modem with GSM.begin()
  // attach the shield to the GPRS network with the APN, login and password
  MODEM.sendf("AT+CMEE=2");
  MODEM.waitForResponse(6000);
  while (!connected) {
    if ((nbAccess.begin(PINNUMBER, apn, user, pass) == NB_READY) &&
        (gprs.attachGPRS() == GPRS_READY)) {
      Serial.println("Connected Now");
      connected = true;
    } else {
      Serial.println("Not connected");
      delay(1000);
    }
  }

  Serial.println("You're connected to the network");  
}
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

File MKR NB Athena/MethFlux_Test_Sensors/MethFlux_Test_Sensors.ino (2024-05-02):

/*
This is a test to see if the sensors are responding to one another. 
I'm so hungry they got me doing slave work over here. 
 */
#include <Arduino.h>
#include <SensirionI2cSfmSf06.h>
#include <Wire.h>
#include <Adafruit_Sensor.h>
#include "Adafruit_BME680.h"
#include "ADS1X15.h"

// macro definitions -------------------------------------
// make sure that we use the proper definition of NO_ERROR
#ifdef NO_ERROR
#undef NO_ERROR
#endif
#define NO_ERROR 0

SensirionI2cSfmSf06 sensor;

static char errorMessage[64];
static int16_t error;

void print_byte_array(uint8_t* array, uint16_t len) {
    uint16_t i = 0;
    Serial.print("0x");
    for (; i < len; i++) {
        Serial.print(array[i], HEX);
    }
}

// -----------------------BME DEF-----------------------------
#define BME_A_ADDRESS 0x76
#define BME_B_ADDRESS 0x77
Adafruit_BME680 A_bme;
Adafruit_BME680 B_bme;


// -----------------------ADC DEF-----------------------------
ADS1115 A_ADS(0x48);
ADS1115 B_ADS(0x49);

void setup() {
    Serial.begin(115200);
    while (!Serial) {
        delay(100);
    }
    Wire.begin();
     // ----------------------------------------- FML -----------------------------------------
    sensor.begin(Wire, SFM4300_I2C_ADDR_2A);

    sensor.stopContinuousMeasurement();
    delay(100);
    uint32_t productIdentifier = 0;
    uint8_t serialNumber[8] = {0};
    error = sensor.readProductIdentifier(productIdentifier, serialNumber, 8);
    if (error != NO_ERROR) {
        Serial.print("Error trying to execute readProductIdentifier(): ");
        errorToString(error, errorMessage, sizeof errorMessage);
        Serial.println(errorMessage);
        return;
    }
    Serial.print("productIdentifier: ");
    Serial.print(productIdentifier);
    Serial.print("\t");
    Serial.print("serialNumber: ");
    print_byte_array(serialNumber, 8);
    Serial.println();
    error = sensor.startO2ContinuousMeasurement();
    if (error != NO_ERROR) {
        Serial.print(
            "Error trying to execute startO2ContinuousMeasurement(): ");
        errorToString(error, errorMessage, sizeof errorMessage);
        Serial.println(errorMessage);
        return;
    }
  // ----------------------------------------- BME -----------------------------------------
  if (!A_bme.begin(BME_A_ADDRESS)) {
   Serial.println("Could not find a valid A_BME680 sensor, check wiring!");
   while(1);
  }
  
  if (!B_bme.begin(BME_B_ADDRESS)) {
   Serial.println("Could not find a valid B_BME680 sensor, check wiring!");
   while(1);
  }

  // Set up oversampling and filter initialization
  A_bme.setTemperatureOversampling(BME680_OS_8X);
  A_bme.setHumidityOversampling(BME680_OS_4X);
  A_bme.setPressureOversampling(BME680_OS_2X);
  A_bme.setIIRFilterSize(BME680_FILTER_SIZE_3);
  A_bme.setGasHeater(320, 150); // 320*C for 150 ms

  B_bme.setTemperatureOversampling(BME680_OS_8X);
  B_bme.setHumidityOversampling(BME680_OS_4X);
  B_bme.setPressureOversampling(BME680_OS_2X);
  B_bme.setIIRFilterSize(BME680_FILTER_SIZE_3);
  B_bme.setGasHeater(320, 150); // 320*C for 150 ms
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

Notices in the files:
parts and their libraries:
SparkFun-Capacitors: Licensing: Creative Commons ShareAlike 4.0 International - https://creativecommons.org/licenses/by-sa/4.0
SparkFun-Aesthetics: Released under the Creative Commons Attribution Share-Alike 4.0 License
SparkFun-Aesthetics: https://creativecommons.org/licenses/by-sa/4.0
